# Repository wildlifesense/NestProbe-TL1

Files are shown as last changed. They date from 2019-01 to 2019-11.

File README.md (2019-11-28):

# NestProbe TL1

This repository has moved to [https://github.com/NikosVallianos/NestProbe/TL1](https://github.com/NikosVallianos/NestProbe/TL1)

I've used the TL1 reliably for over a year, but have also stared developing the TL2, which uses the Si7051 temperature sensor and the ATtiny816 MCU.
The NestProbe TL1 is a low cost, high accuracy, long-life temperature logger
developed at Wildlife Sense for sea turtle egg incubation research. This repository

Some aspects and decisions during development have been documented at [hackaday.io/project/27560-low-costpowersize-temperature-logger](https://hackaday.io/project/27560-low-costpowersize-temperature-logger).

The main components in the TL1 are:

| Component          | Model       |
|:-------------------|:------------|
| Microcontroller    | ATmega328PB |
| Temperature sensor | MAX30205    |
| EEPROM Memory      | AT25DN512C  |
| Crystal oscillator | ECS-.327-7-34B-C-TR (32.768kHz) |
| Battery type       | CR2032      |

Plus one SMD 0402 LED and a small number of pull-up resistors and decoupling capacitors.

The WSTL18 firmware and Eagle files are released under the GNU General Public
License version 3. This roughly means that you can use these files and designs,
manufacture the TL1 or derivatives and even sell them but you always have to
make the original source code or derivatives available under the same license.
See COPYING for details.

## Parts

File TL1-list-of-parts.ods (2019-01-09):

Part # | Qty | Used at | Name | Value | Dimension | Type | Manufacturer | Supplier | Price | Total | Bulk Qty | Bulk Price | Bulk Total
ATMEGA328PB-MN | 1 | MCU | MCU | 20MHz 32k | 5x5mm QFN-32 | CMOS | Atmel | Mouser | 1.120 € | 1.120 € | 50 | 1.030 € | 51.500 €
MAX30205MTA+ | 1 | Temperature sensor | TMP |  | 4x4mm TDFN-8 |  | Maxim | Mouser | 1.530 € | 1.530 € | 50 | 1.410 € | 70.500 €
AT25DN512C-XMHF-B | 1 | EEPROM memory | EEPROM | 512k | 3x6.4 TSSOP-8 | EEPROM | Adesto | Mouser | 0.315 € | 0.315 € | 50 | 0.265 € | 13.250 €
ECS-.327-7-34B-C-TR | 1 | 32.768kHz crystal | T1 | 32.768kHz 10ppm | 3.2x1.5 |  | ECS | Mouser | 0.621 € | 0.621 € | 50 | 0.513 € | 25.650 €
APHHS1005SYCK | 1 | Yellow LED indicator | LED0 | 590nm, 150mCd | 0402 | Yellow/clear | Kingbright | Mouser | 0.221 € | 0.221 € | 50 | 0.138 € | 6.900 €
BAT-HLD-001 | 1 | Battery holder |  | CR2032 | 2032 | Metal | Linx | Mouser | 0.238 € | 0.238 € | 50 | 0.218 € | 10.900 €
GRM155R61C104KA88D | 5 | Decoupling capacitors | C1, C2, C3, C4, C5 | 0.1uF | 0402 | Multilayer X5R | Murata | Mouser | 0.085 € | 0.425 € | 100 | 0.006 € | 0.600 €
RC0402JR-0710KL | 1 | Reset pull-up | R1 | 10k | 0402 | Thick film | Yageo | Mouser | 0.085 € | 0.085 € | 100 | 0.002 € | 0.200 €
RC0402JR-0768RL | 1 | LED current limiter | R5 | 68Ω | 0402 | Thick film | Yageo | Mouser | 0.085 € | 0.085 € | 100 | 0.002 € | 0.200 €
RC0402FR-074K7L | 3 | TWI pull-up | R2, R3, R4 | 4.7k | 0402 | Thick film | Yageo | Mouser | 0.085 € | 0.255 € | 200 | 0.003 € | 0.600 €

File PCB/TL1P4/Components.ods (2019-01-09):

Name | Value | Size | Quantity | Part No. |  | Price (1) | Qty | Price (Qty) | Cost | 18/4/2018
MCU | ATmega328PB | VQFN32 | 1 | ATMEGA328PB-MN | Atmel | 1.270 € | 50 | 1.030 € | 51.50 €
TMP | MAX30205 | TDFN8 | 1 | MAX30205MTA+ | Maxim | 1.480 € | 50 | 1.360 € | 68.00 €
MEM | AT25DN512C | TSSOP-8 | 1 | AT25DN512C-XMHF-B | Adesto | 0.303 € | 50 | 0.256 € | 12.80 €
BAT | BAT-HLD-001-THM | CR2032 | 1 | BAT-HLD-001-THM | Linx | 0.230 € | 50 | 0.211 € | 10.55 € | 10
T1 | ABS07AIG | 3.2mm x 1.5mm | 1 | ABS07AIG-32.768kHz-7-1-T | Abracon | 0.951 € | 50 | 0.779 € | 38.95 €
R1 | 10k 5% | 0201 | 1 | AC0201FR-0710KL | Yageo | 0.172 € | 100 | 0.014 € | 1.40 € | 100
R2, R3, R4 | 4.7k | 0201 | 3 | RC0201FR-074K75L | Yageo | 0.082 € | 300 | 0.008 € | 2.40 € | 300
R5 | 68Ω 5% | 0201 | 1 | RC0201JR-0768RL | Yageo | 0.082 € | 100 | 0.006 € | 0.60 € | 100
C1, C2, C3, C4, C5 | 0.1uF | 0201 | 5 | GRM033R60J104JE19D | Murata | 0.082 € | 500 | 0.007 € | 3.50 € | 500
LED0 | Amber | 0402 | 1 | APHHS1005SYCK | Kingbright | 0.213 € | 100 | 0.098 € | 9.80 € | 100
C6, C7 | Not used | 0402 | 0

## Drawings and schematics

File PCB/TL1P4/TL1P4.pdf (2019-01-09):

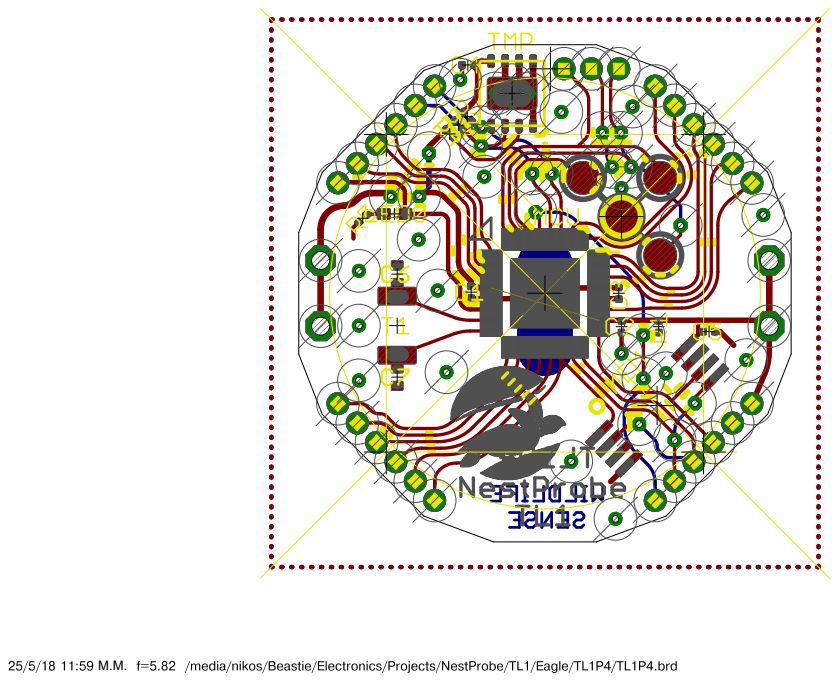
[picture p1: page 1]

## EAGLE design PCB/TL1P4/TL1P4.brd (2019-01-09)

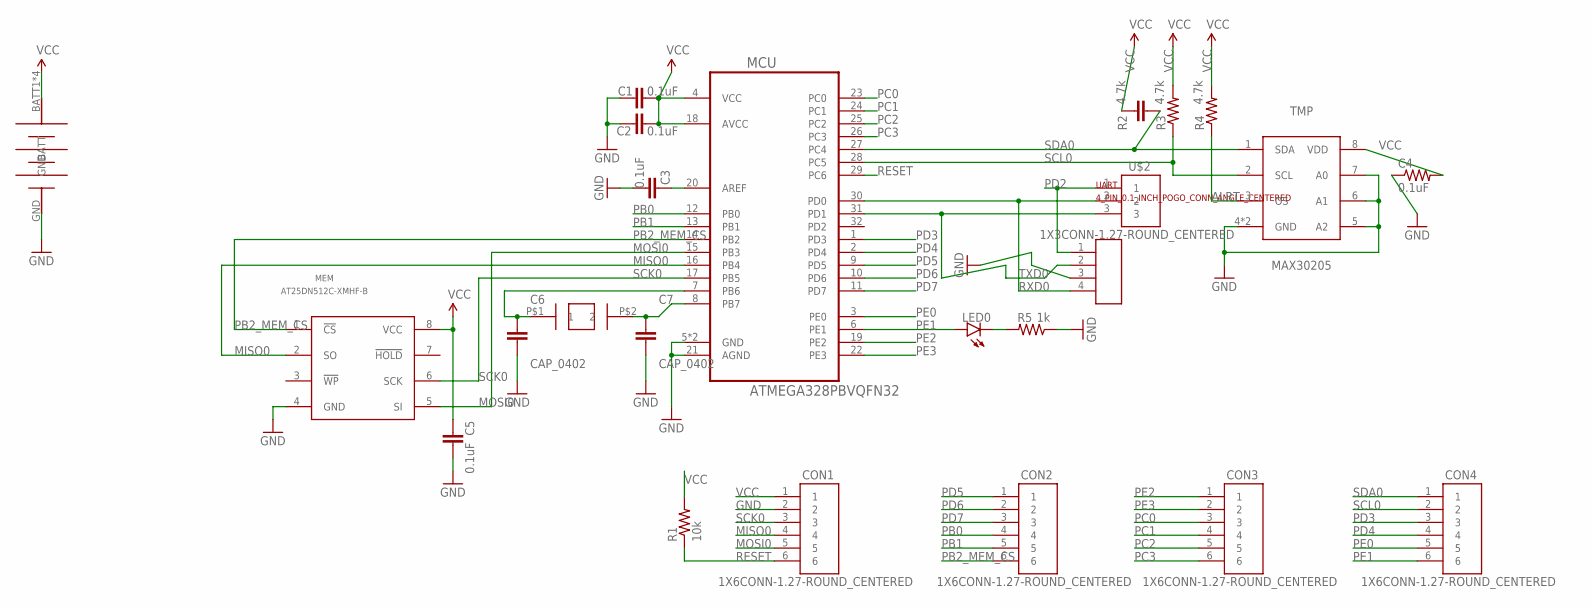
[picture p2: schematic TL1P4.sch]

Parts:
C1, C2, C3, C4, C5: 0.1uF; RES_CAP_0201
C6, C7: CAP_0402; SMD_0402
CON1, CON2, CON3, CON4: 1X6CONN-1.27-ROUND_CENTERED; 1X6_1.27_ROUND_CENTERED
LED0: LED_0402
MCU: ATMEGA328PBVQFN32; ATMEGA328PB_VFQFN32
MEM: AT25DN512C-XMHF-B; TSSSOP-8
R1: 10k; RES_CAP_0201
R2, R3, R4: 4.7k; RES_CAP_0201
R5: 1k; RES_CAP_0201
T1: ABS07AIG
TMP: MAX30205; MAX30205_TDFN8
U$1: LINX-CR2032-BAT-HLD-THM; CR2032-LINX-THM
U$2: 1X3CONN-1.27-ROUND_CENTERED; 1X3_1.27_ROUND_CENTERED
UART: 4_PIN_0.1_INCH_POGO_CONN_ANGLE_CENTERED; 4_PIN_0.1"_POGO_ANGLE_CENTERED

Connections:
ALRT: R4.2, TMP.3 (OS)
AREF: C3.1, MCU.20 (AREF)
GND: C1.2, C2.2, C3.2, C4.2, C5.2, C6.2, C7.2, CON1.2, MCU.5 (GND), MCU.21 (AGND), MCU.PAD (GND), MEM.4 (GND), R5.2, TMP.4 (GND), TMP.5 (A2), TMP.6 (A1), TMP.7 (A0), TMP.PAD (GND), U$1.GND, UART.3
MISO0: CON1.4, MCU.16 (PB4), MEM.2 (SO)
MOSI0: CON1.5, MCU.15 (PB3), MEM.5 (SI)
unnamed: C7.1, MCU.8 (PB7), T1.P$2 (2)
unnamed: C6.1, MCU.7 (PB6), T1.P$1 (1)
unnamed: LED0.CATHODE (C), R5.1
PB0: CON2.4, MCU.12 (PB0)
PB1: CON2.5, MCU.13 (PB1)
PB2_MEM_CS: CON2.6, MCU.14 (PB2), MEM.1 (!CS!)
PC0: CON3.3, MCU.23 (PC0)
PC1: CON3.4, MCU.24 (PC1)
PC2: CON3.5, MCU.25 (PC2)
PC3: CON3.6, MCU.26 (PC3)
PD2: U$2.1, UART.1
PD3: CON4.3, MCU.1 (PD3)
PD4: CON4.4, MCU.2 (PD4)
PD5: CON2.1, MCU.9 (PD5)
PD6: CON2.2, MCU.10 (PD6)
PD7: CON2.3, MCU.11 (PD7)
PE0: CON4.5, MCU.3 (PE0)
PE1: CON4.6, LED0.ANODE (A), MCU.6 (PE1)
PE2: CON3.1, MCU.19 (PE2)
PE3: CON3.2, MCU.22 (PE3)
RESET: CON1.6, MCU.29 (PC6), R1.2
RXD0: MCU.30 (PD0), U$2.2, UART.4
SCK0: CON1.3, MCU.17 (PB5), MEM.6 (SCK)
SCL0: CON4.2, MCU.28 (PC5), R3.2, TMP.2 (SCL)
SDA0: CON4.1, MCU.27 (PC4), R2.2, TMP.1 (SDA)
TXD0: MCU.31 (PD1), U$2.3, UART.2
VCC: C1.1, C2.1, C4.1, C5.1, CON1.1, MCU.4 (VCC), MCU.18 (AVCC), MEM.8 (VCC), R1.1, R2.1, R3.1, R4.1, TMP.8 (VDD), U$1.BATT1 (BATT), U$1.BATT2 (BATT), U$1.BATT3 (BATT), U$1.BATT4 (BATT)

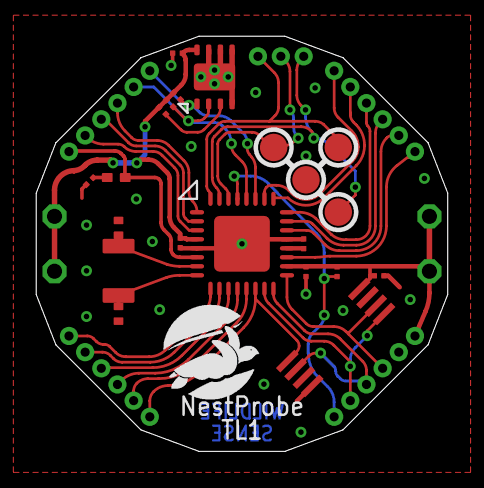
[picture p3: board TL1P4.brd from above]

Board: 2 copper layers, 22.9 x 23.1 mm, 24 parts (1 on the bottom side), 32 nets.

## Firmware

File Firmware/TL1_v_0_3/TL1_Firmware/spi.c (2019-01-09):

/********************************************************************************

  spi.c: SPI module of NestProbe TL1 firmware.
 
  Copyright (C) 2017 Nikos Vallianos <nikos@wildlifesense.com>
  
  This file is part of NestProbe TL1 firmware.
  
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
  ********************************************************************************/
#include <avr/io.h>
#include <avr/interrupt.h>
#include "spi.h"

// #################### PORTS & PINS FOR SPI0. Don't change unless porting to another mcu ####################
//	MISO0 is PB4
//	SCK0 is PB5
//	MOSI0 is PB3
//	SS0 is PB2

// Initialize pins for spi communication
void spiEnable(void) {
	DDRB &= ~(1<<DDRB4);		// MISO is INPUT
	PORTB &= ~(1<<PORTB4);		// No pull (tri-state for inputs?)
	
	DDRB |= (1<<DDRB3);			// MOSI output
	PORTB &= ~(1<<PORTB3);		// Low

	DDRB |= (1<<DDRB5);			// SCK out
	PORTB &= ~(1<<PORTB5);		// Low

    PRR0 &= ~(1<<PRSPI0);								// Clock SPI0 clock, powers the module
	
	SPCR0 = (1<<SPE) | (1<<MSTR) | (0<<SPR1) | (0<<SPR0);		// Enable SPI, set to Master, set prescaler.
}

/*
 * spiDisable: Disable the SPI module and set it for lowest power consumption.
 * TODO: Add some fault detection: SPSR0.WCOL0
 */
void spiDisable(void) {
	SPCR0 = 0;											// Disable SPI.
	PRR0 |= (1<<PRSPI0);								// Cut off SPI0 clock, shuts the module	
	DDRB  &= ~(1<<DDRB3|1<<DDRB4|1<<DDRB5);				// MOSI0, SCK0, MISO0 pins are input
	PORTB |=  (1<<PORTB3|1<<PORTB4|1<<PORTB5);			// Pull-up enabled, reduces consumption.
}

// When a serial transfer is complete, the SPIF flag is set.
uint8_t spiTradeByte(uint8_t byte) {
	SPDR0 = byte;										
	loop_until_bit_is_set(SPSR0, SPIF);			
	return SPDR0;
}



// Shift an array out and retain returned data.
void spiExchangeArray(uint8_t * dataout, uint8_t * datain, uint8_t len) {
	for (uint8_t i = 0; i < len; i++) {
		datain[i] = spiTradeByte(dataout[i]);
	}
}



// Shift an array out and discard returned data.
void spiTransmitArray(uint8_t * dataout, uint8_t len) {
	for (uint8_t i = 0; i < len; i++) {
		spiTradeByte(dataout[i]);
	}
}

// Shift an array in while sending scrap data
void spiReceiveArray(uint8_t * datain, uint8_t len) {
	for (uint8_t i=0; i<len; i++) {
		datain[i] = spiTradeByte(0x00);
	}
}

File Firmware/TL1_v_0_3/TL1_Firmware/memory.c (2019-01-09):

/********************************************************************************

 memory.c

	This module was written for Atmel's ATmega328PB using Adesto's AT25DN512C
	512kbit SPI serial EEPROM. It was designed for memory and power optimization
	and	does not contain generalizations.

	Temperature logs consist of a settings byte, a timestamp, and a string
	of two-byte temperatures. Logs always begin at the first byte of a
	memory page, so only the first two [FEW?] bytes of each page need to be read
	to locate a start signature. Logs continue on through as many memory
	pages as necessary until the log stops or the memory array is full.
	There is no log end signature, as the log may terminate abruptly due to
	battery failure, corrosion, or a stop command via UART from the user.
	Although not recommended, the user can choose to begin a new log
	without erasing existing logs on the memory. In such a case, the system
	will locate the end of the last log in memory, skip any remaining bytes
	on the last memory page used, and begin a new log at the first byte of
	the next memory page.  The system does not allow the deletion of
	individual logs; this would cause fragmentation of the memory array and
	would require larger firmware programs to be handled. In stead, this
	system is aimed for simplicity.

	Author/Copyright: Nikos Vallianos (C) 2017.

	This module was developed for the NestProbe TL1 temperature logger.

	Settings byte:
		Interval:

 
  Copyright (C) 2017 Nikos Vallianos <nikos@wildlifesense.com>
 
  This file is part of NestProbe TL1 firmware.
 
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
********************************************************************************/
#include <avr/io.h>
#include <util/delay.h>
#include "spi.h"
#include "uart.h"		// Debugging use only
#include "memory.h"


// Flash parameters
#define MEMORY_ARRAY_ADDRESS_FIRST		0x000000	// Address of first byte in memory array. Can be moved up to make room for settings.
#define MEMORY_ARRAY_ADDRESS_LAST		0x00FFFF	// Address of last byte in memory array.
#define MEMORY_PAGE_FIRST				0x00		// Number of first page in memory array used.
#define MEMORY_PAGE_LAST				0xFF		// Number of last page in memory array used.
#define MEMORY_PAGE_SIZE				256			// Number of bytes in a memory page.

#define MEMORY_GET_BYTE(ADDRESS)		(0xFF & ADDRESS)			// Return byte within page, 0x00-0xFF
#define MEMORY_GET_PAGE(ADDRESS)		((0xFF00 & ADDRESS) >> 8)	// Return page, 0x00-0xFF

#define MEMORY_BUSY_LIMIT	1000				// "Busy" status time read before flagging. 
uint8_t memory_status_byte_1;					// Every time Status Register 1 is read, it's also saved here.
uint8_t memory_status_byte_2;					// Every time Status Register 2 is read, it's also saved here.
uint8_t memory_manufacturer_id;					// First byte output after "read manufacturer and device id" opcode is clocked in.
uint16_t memory_device_id;						// Subsequend two bytes output after "read manufacturer and device id" opcode is clocked in.

#define MEMORY_OTP_ARRAY_LENGTH 128
uint8_t memory_OTP_array[MEMORY_OTP_ARRAY_LENGTH];

// Read commands
//													address	Dummy	Data	MHz
#define	MEMORY_READ_ARRAY_FAST		0x0B		//	3		1		1+		104
#define	MEMORY_READ_ARRAY_SLOW		0x03		//	3		0		1+		33

// Erase
#define MEMORY_ERASE_PAGE			0x81		//	3		0		0		104 Time 6-20ms.
#define	MEMORY_ERASE_BLOCK_4K		0x20		//	3		0		0		104 Time 35-50ms.
#define	MEMORY_ERASE_BLOCK_32K		0x52		//	3		0		0		104 Time 250-350ms.
#define MEMORY_ERASE_BLOCK_32K_ALT	0xD8		//	3		0		0		104 Time 250-350ms.
#define MEMORY_ERASE_CHIP_1			0x60		//	0		0		0		104 Time 500-700ms.
#define MEMORY_ERASE_CHIP_2			0xC7		//	0		0		0		104 Time 500-700ms.
#define MEMORY_ERASE_CHIP_3_OLD		0x62		//	0		0		0		104	Time 500-700ms. Legacy command, do not use.

// Byte / Page Program, 1 to 256 bytes
#define MEMORY_PROGRAM				0x02		//	3		0		1+		104		1 to 256 bytes, page overrun rewinds to start!

#define MEMORY_WRITE_ENABLE			0x06		//	0		0		0		104
#define MEMORY_WRITE_DISABLE		0x04		//	0		0		0		104

// Security register
#define MEMORY_PROGRAM_OTP_SECURITY_REGISTER	0x9B		//	3		0		1+		104
#define MEMORY_READ_OTP_SECURITY_REGISTER		0x77		//	3		2		1+		104

// Status

#define MEMORY_READ_STATUS_REGISTER				0x05		//	0		0		1+		104
#define MEMORY_WRITE_STATUS_REGISTER_BYTE_1		0x01		//	0		0		1		104
#define MEMORY_WRITE_STATUS_REGISTER_BYTE_2		0x31		//	0		0		1		104

// Device ID
#define MEMORY_RESET							0xF0		//	0		0		1(0xD0)	104		0xD0 confirms reset.
#define MEMORY_CONFIRM_RESET					0xD0		//	0		0		0		104
#define MEMORY_READ_MANUFACTURER_AND_DEVICE_ID	0x9F		//	0		0		1-4		104
#define MEMORY_READ_ID_LEGACY					0x15		//	0		0		2		104		Legacy

// Power down
#define MEMORY_DEEP_POWER_DOWN					0xB9		//	0		0		0		104
#define MEMORY_RESUME_FROM_DEEP_POWER_DOWN		0xAB		//	0		0		0		104
#define MEMORY_ULTRA_DEEP_POWER_DOWN			0x79		//	0		0		0		104

// Status Register 1
#define MEMORY_SR1_BPL		7		// [R/W] Block protection locked. 0: BP0 bit unlocked (def). 1: BP0 locked in current state when _WP_ asserted.
// Bit 6 reserved for future use.
#define MEMORY_SR1_EPE		5		// [R] 0: Erase or program operation was successful. 1: Erase or program error detected.
#define MEMORY_SR1_WPP		4		// [R] 0: _WP_ is asserted. 1: _WP_ is deasserted.
// Bit 3 reserved for future use.
#define MEMORY_SR1_BP0		2		// [R/W] 0: Entire memory array is unprotected. 1: Entire memory array is protected.
#define MEMORY_SR1_WEL		1		// [R] 0: Device is not write enabled (default). 1: Device is write enabled.
#define MEMORY_SR1_BSY		0		// [R] 0: Device is ready. 1: Device is busy with an internal operation.

// Status Register 2
// Bit 7 reserved for future use.
// Bit 6 reserved for future use.
// Bit 5 reserved for future use.
#define MEMORY_SR2_RSTE		4		// [R/W] 0: Reset command is disabled (default). 1: Reset command is enabled.
// Bit 3 reserved for future use.
// Bit 2 reserved for future use.
// Bit 1 reserved for future use.
#define MEMORY_SR2_BSY		0		// [R] 0: Device is ready. 1: Device is busy with an internal operation.

// Timing definitions from AT25DN512C datasheet.
//							usec
#define MEMORY_TIME_EDPD	2		// Maximum Chip Select high to deep power-down.
#define MEMORY_TIME_EUDPD	3		// Maximum Chip Select high to ultra-deep power-down (*)
#define MEMORY_TIME_SWRST	50		// Maximum software reset time.
#define MEMORY_TIME_CSLU	0.02	// Minimum Chip Select low to exit ultra-deep power-down
#define MEMORY_TIME_XUDPD	70		// Minimum exit ultra-deep power-down time
#define MEMORY_TIME_RDPD	8		// Maximum Chip Select high to standby mode. (from Deep power-down)

#define MEMORY_TIME_PP		1750	// Maximum Page Program time (256 Bytes)
#define MEMORY_TIME_BP		8		// Typical byte program time
#define MEMORY_TIME_PE		20000	// Maximum page erase time
#define MEMORY_TIME_BLKE4	50000	// Maximum 4Kbytes block erase time
#define MEMORY_TIME_BLKE32	350000	// Maximum 32Kbytes block erase time
#define MEMORY_TIME_CHPE	700000	// Maximum Chip Erase time
#define MEMORY_TIME_OTPP	950		// Maximum OTP Security Register program time
#define MEMORY_TIME_WRSR	40000	// Maxirum Write Status Register time
#define MEMORY_TIME_VCSL	70		// Minimum Vcc to Chip Select Low time
#define MEMORY_TIME_PUW		5000	// Max Power-up device delay before Program or Erase Allowed
// Also, device will perform a Power-On-Reset at 2.2V.



uint8_t memory_flags;						// Memory-related flags set by this module. See MEMORY_FLAG_xxxxx definitions below.

// Bits in this module's memory_flags variable and what they mean.
#define MEMORY_FLAG_FULL			7		// Memory is full.
#define MEMORY_FLAG_PROGRAM_ERROR	6		// Program error occurred on memory chip.
#define MEMORY_FLAG_BUSY_TIMEOUT	5		// Memory was busy for longer than timeout.
#define MEMORY_FLAG_OVERWRITE		4		// Recorded a temperature log on memory that wasn't erased (0xFF).
#define MEMORY_FLAG_FIRMWARE_ERROR	3		// Some sort of firmware error.
#define MEMORY_FLAG_2				2		// Something even different
#define MEMORY_FLAG_1				1		// Even more
#define MEMORY_FLAG_0				0		// Last


/*************************** Internal Functions *******************************/
/*
 * Send a single opcode to the memory chip. Works with all commands
 * that don't require any address or dummy bytes and don't return
 * any data back (write enable/disable and power down commands).
 */
void _memorySingleCommand(uint8_t command) {
	MEMORY_CS_SELECT;
	spiTradeByte(command);
	MEMORY_CS_DESELECT;
}

/*
 *  Send a 3-byte address to the flash unit. This function takes a
 *	two-byte input and adds the third 0x00 since that's always 0x00 on this module.
 */
void _memorySendAddress(uint16_t address) {
	uint8_t address_page = (uint8_t)(address>>8);
	uint8_t address_byte = (uint8_t) address;
	spiTradeByte(0x00);								// Send most significant byte first.
	spiTradeByte(address_page);						// Then send middle significant byte.
	spiTradeByte(address_byte);						// Then send least significant byte.
}

/*
 * Send dummy_size zeros over to the flash memory.
 */
void _memorySendDummy(uint8_t dummy_size) {
	for (uint8_t i=0; i<dummy_size; ++i) {
		spiTradeByte(0);
	}
}


/*
 *	Set the flag to indicate said error occurred.
 *	This is only for internal module use and has nothing to do
 *	with the actual memory chip.
 */
void _memoryFlagSet(uint8_t flag_position) {
	memory_flags |= (1<<flag_position);
}

/*
 * Unset the flag to indicate said error didn't occur or was addressed.
 */
void _memoryFlagClear(uint8_t flag_position) {
	memory_flags &= ~(1<<flag_position);
}

/*
 * Clear all flags to set module flags in reset state.
 */
void _memoryFlagClearAll(void) {
	memory_flags = 0;
}

/*
 * Check if memory chip is busy with a program or erase.
 * Returns 1 if memory is busy, 0 if it is available.
 */
uint8_t _memoryBusy(void) {
	MEMORY_CS_SELECT;
	spiTradeByte(MEMORY_READ_STATUS_REGISTER);
	memory_status_byte_1 = spiTradeByte(MEMORY_READ_STATUS_REGISTER);		// Does this work?
	MEMORY_CS_DESELECT;
	return (memory_status_byte_1 & (1<<MEMORY_SR1_BSY));
}
/*
 * Check if memory chip is busy and wait for a bit. If wait is too long, register
 * relevant flag and stop waiting.
 * This function should be used at top of every program/erase function.
 */
void _memoryCheckBusy(void) {
	uint16_t memory_busy_counter = 0;
	while(_memoryBusy() && (memory_busy_counter < MEMORY_BUSY_LIMIT)) {	// Wait until memory is not busy.
		++memory_busy_counter;
		_delay_us(10);
	}
	if (memory_busy_counter >= MEMORY_BUSY_LIMIT) {
		_memoryFlagSet(MEMORY_FLAG_BUSY_TIMEOUT);
	}
}

/*
 * Enable a reset operation by setting the RSTE bit in status register 2.
 */
void _memoryResetEnable(void) {
	_memorySingleCommand(MEMORY_WRITE_ENABLE);
	MEMORY_CS_SELECT;
	spiTradeByte(MEMORY_WRITE_STATUS_REGISTER_BYTE_2);
	spiTradeByte(1<<MEMORY_SR2_RSTE);
	MEMORY_CS_DESELECT;
	_memorySingleCommand(MEMORY_WRITE_DISABLE);
}


/*
 * Do a memory operation reset while memory is busy.
 * This stops any program or erase operation currently in progress.
 * The contents of the page currently being written cannot be guaranteed
 * after a reset operation.
 */
void _memoryResetOperation(void) {
	MEMORY_CS_SELECT;
	spiTradeByte(MEMORY_RESET);
	spiTradeByte(MEMORY_CONFIRM_RESET);
	MEMORY_CS_DESELECT;
}
/*********************** End Internal Functions *******************************/


/*********************** Begin Public Functions *******************************/

/*
	memoryInit: Initialize the memory chip for first use after power-up and until
	the logger is power-cycled.
 */
void memoryInitialize(void) {
	MEMORY_CS_INIT;						// Set memory pin as output.
	MEMORY_CS_DESELECT;					// Init but don't assert yet.
	
	memory_flags = 0;					// Clear memory flags.
	spiEnable();
	memoryReadStatusRegisters();		// Read memory chip status registers into module.
	memoryReadMFDID();					// Read memory chip manufacturer and device ids.
	spiDisable();
}
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

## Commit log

2019-01-09 Added list of parts
    [TL1-list-of-parts.ods]
2019-01-09 Removed few gerber files
    [TL1P4.GTL, TL1P4.GTO, TL1P4.GTP, TL1P4.GTS]
2019-01-09 Removed some more gerber files
    [TL1P4.GBL, TL1P4.GBO, TL1P4.GBP, TL1P4.GBS]
2019-01-09 Formatted prices and costs to currency.
    [Components.ods]

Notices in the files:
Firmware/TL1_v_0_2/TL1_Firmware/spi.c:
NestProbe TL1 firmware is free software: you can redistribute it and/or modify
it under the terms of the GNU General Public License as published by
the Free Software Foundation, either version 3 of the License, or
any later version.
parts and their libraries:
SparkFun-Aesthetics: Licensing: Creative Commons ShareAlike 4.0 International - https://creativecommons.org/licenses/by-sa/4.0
